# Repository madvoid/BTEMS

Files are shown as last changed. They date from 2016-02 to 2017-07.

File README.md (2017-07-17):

# BTEMS
This is the repository for the BTEMS Sensor Stations. A majority of the documentation is in this file, but some is in the code.

### Uploading Instructions
First, change the `XX` in the filename on line 26 to whatever the BTEMS identifier code is. The current methodology is to use a two digit hexadecimal number. Then, using a 3.3v FTDI programmer such as [this](https://www.adafruit.com/products/284) or [this](https://www.sparkfun.com/products/9873), upload BTEMS.ino to a BTEMS. In the Arduino IDE 'tools' menu, the board should be set to `Arduino Pro or Pro Mini`, the processor should be set to `ATmega328 (3.3V, 8Mhz)`, and the programmer should be set to whatever programmer is used. `AVRISP mkll` often works. The port should be set to whatever port the Arduino is plugged into. The power switch on the BTEMS should be set to off when programming.

### Running Instructions
Place the BTEMS where measurements should take place. Ensure there's an SD card inserted into the SD slot. Turn the switch from 'OFF' to 'ON'. After ~3 seconds, the green LED will turn on and remain lit for ~2 seconds. From then on, the BTEMS is running. The green LED should blink every ~10 seconds, implying a measurement was taken. If a red light comes on after turning on, the likely culprit is either the SD card or the real time clock. Make sure the SD card works and has space, and make sure the real time clock works and has a backup battery plugged in.

To turn off, wait until the green LED blinks, then turn the switch from 'ON' to 'OFF' soon after. It is important to wait until the LED is finished blinking to make sure the file is successfully saved.

### File Descriptions
* BTEMS/
 * `BTEMS.ino` - BTEMS arduino sketch
 * `SHT2x.h` - SHT21 library header
 * `SHT2x.cpp` - SHT21 library file
* BTEMS PCB/
 * `BTEMS.brd` - Eagle board file for BTEMS PCB
 * `BTEMS.sch` - Eagle schematic file for BTEMS PCB
 * `BTEMS.*.ger` - BTEMS gerber files for manufacturing
 * `BTEMS.*.xln` - More BTEMS manufacturing files
 * `eagle.epf` - Eagle preferences file
* Data Sheets/
 * Contain part data sheets for posterity
* Matlab Scripts/
 * `Battery_Analysis.m` - Estimates the battery life given certain assumptions.
 * `BTEMS_Plotter.m` - Requests a BTEMS output .csv file from the user and plots some common plots. Very simple
* Radiation Shield/
 * `Radiation_Shield_RevD.*` - The CAD files for the radiation shield. Edit the .SLDPRT file, submit the .STL file for 3D printing, and view the .pdf file. The .STL file can be easily previewed within Github.
 * `SHT_Plug.*` - The CAD files for the plug that holds the SHT21. Edit the .SLDPRT file, submit the .STL file for 3D printing, and view the .pdf file. The .STL file can be easily previewed within Github
* `Bill of Materials.xlsx` - BTEMS bill of materials. Should be 99.9% complete. Missing any mounting hardware or insulation materials.

### Troubleshooting
* Red Light: SD card problem. Is there an SD card? Is it working? Is it formatted? 
 * In one instance, one of the batteries leaked, leaving residue all over the battery holder. The unit would turn on, but a new file would not be able to be created, and the red light would show. After cleaning the residue and replacing the batteries, the unit worked. It is suspected that the residue limited the amount of current available to the unit, which prevented the SD card from working properly.
* No Lights: Possible sensor problem. Are they plugged in? Are they good? Are they plugged in backwards?

### To-Do
1. Measurement validation

### Notes
* Heat ruins the battery life. Outdoor BTEMS will perform poorly compared to the indoor ones.

### Assembly Instructions
1. Solder SD card holder to PCB
2. Solder female RTC header to PCB
3. Solder four male header pins to RTC in the PWR, GND, SCL, SDA holes
4. Solder resistors in corect place
5. Solder power switch in place
6. Solder power screw terminal in place. Make sure screw terminal is straight and fits flush on the PCB!
7. Solder Arduino in place. The programming header on the Arduino should be near on the side of the power switch. Use regular male headers, and the long side of the headers should be pointing up from the board. Make sure all the pins on the Arduino, especially the four pins in the middle of the arduino, are passed through to the PCB.
8. Solder male headers for sensor plug ins in place
   Detail to be added...

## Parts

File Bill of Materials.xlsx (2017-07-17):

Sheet: Full Instrument
Number of Prototypes: |  | 1 | Shipping Costs Not Included! |  |  |  |  |  |  |  |  |  |  |  |  |  |  | BTEMS Required: | 58
Information |  |  |  | Ideal Cost/Unit |  | Ideal Cost/10 Units |  | Ideal Cost/25 Units |  | Ordering |  |  |  | Notes | Cost Percentage Breakdown |  |  | 6/22/2016 Order
Number | Part | Part Name | Quantity/Instrument | Cost/Part | Prototype Cost | Cost/Part | Prototype Cost | Cost/Part | Prototype Cost | Source | Part Number | Package | Link |  | 1 Unit | 10 Units | 25 Units | Quantity Ordered | Cost/Unit | Total Cost
 | Surface Temp Sensor | MLX90614 | 1 | $6.50 | $6.50 | $6.50 | $65.00 | $6.50 | $162.50 | Haoyu Electronics | MLX90614 | Breakout Board | http://www.hotmcu.com/infrared-thermometer-mlx90614-breakout-board-p-223.html?cPath=8 |  | 7.90% | 8.16% | 8.23% | 58 | $6.50 | $377.00
 | Temp/Humidity Sensor | SHT21 | 1 | $11.20 | $11.20 | $11.20 | $112.00 | $11.20 | $280.00 | Ebay | N/A | N/A | http://www.ebay.com/itm/1PCS-SHT21-Digital-Humidity-And-Temperature-Sensor-Module-Replace-SHT15-SHT11-/182103356189 | May need alternates. Not reliable source | 13.61% | 14.05% | 14.18% | 58 | $11.20 | $649.60
 | Waterproof Box | N/A | 1 | $10.50 | $10.50 | $10.50 | $105.00 | $10.50 | $262.50 | Rescue Essentials | 50-0336 | N/A | http://www.rescue-essentials.com/1449-00-xs-polycarbonate-waterproof-case/ |  | 12.76% | 13.17% | 13.30% | 58 | $10.50 | $609.00
 | Real Time Clock | DS3231 | 1 | $13.95 | $13.95 | $12.56 | $125.60 | $12.56 | $314.00 | Adafruit | 3013 | Breakout Board | https://www.adafruit.com/product/3013 |  | 16.96% | 15.76% | 15.91% | 58 | $12.56 | $728.48
 | Backup Battery | CR1220 | 1 | $0.87 | $0.87 | $0.79 | $7.88 | $0.79 | $19.70 | Mouser | 658-CR1220 | 1220 | http://www.mouser.com/ProductDetail/Panasonic-Battery/CR1220/?qs=sGAEpiMZZMuuBt6TL7D%2f6A7P4Pabhz5g | Much cheaper if bought in quantities of 50+ | 1.06% | 0.99% | 1.00% | 58 | $0.70 | $40.60
 | AA Batteries | N/A | 8 | $0.23 | $1.80 | $0.23 | $18.00 | $0.23 | $45.00 | Mouser | 658-LR6XWA | AA | http://www.mouser.com/ProductDetail/Panasonic-Battery/LR6XWA-B/?qs=sGAEpiMZZMuXcNZ31nzYhcGI0qUUgbjI14kQITT1Veg%3d | Comes in packs of 500. Digikey has same part for cheaper with smaller quantities if necessary | 2.19% | 2.26% | 2.28% | 0 | $0.23 | $0.00
 | Jumper Wires | N/A | 0.2 | $3.95 | $0.79 | $3.56 | $7.12 | $3.56 | $17.80 | Adafruit | 794 | N/A | https://www.adafruit.com/products/794 | Comes in packs of 40. Only need 8 per BTEMS | 0.96% | 0.89% | 0.90% | 12 | $3.56 | $42.72
 | 4x AA Battery Holder | N/A | 2 | $1.15 | $2.30 | $1.06 | $21.20 | $1.06 | $53.00 | Mouser | 12BH348-GR | N/A | http://www.mouser.com/ProductDetail/Eagle-Plastic-Devices/12BH348-GR/ | Much cheaper if bought in quantities of 100+ | 2.80% | 2.66% | 2.68% | 116 | $0.90 | $104.86
 | SD Card | N/A | 1 | $3.60 | $3.60 | $3.60 | $36.00 | $3.60 | $90.00 | Newegg | 9SIA1EK0HR9980 | Micro SD with Regular Adapter | http://www.newegg.com/Product/Product.aspx?Item=9SIA1EK0HR9980 | Micro SD card but comes with standard size adapter - Not reliable source | 4.38% | 4.52% | 4.56% | 58 | $3.60 | $208.80
 | Full Shield | N/A | 1 | $24.45 | $24.45 | $23.62 | $236.18 | $22.89 | $572.33 | See 'Shield Parts' | N/A | N/A |  | See 'Shield Parts' Sheet for details | 29.72% | 29.63% | 28.99% | N/A | $0.00 | $778.59
 | Break Away Headers - Right Angle | N/A | 0.1 | $1.95 | $0.20 | $1.95 | $1.95 | $1.85 | $4.63 | Sparkfun | PRT-00553 | N/A | https://www.sparkfun.com/products/553 | Comes in strips of 40, currently only need 4/board. Actually used for SHT21 breakout. Other sensor comes with headers | 0.24% | 0.24% | 0.23% | 6 | $1.95 | $11.70
 | Radiation Shield | N/A | 1 | $6.00 | $6.00 | $6.00 | $60.00 | $6.00 | $150.00 | UofU MechE Dept. | N/A | N/A |  | Printed from UofU MechE 3D printer. Maybe cheaper elsewhere? | 7.29% | 7.53% | 7.60% | 0 | $6.00 | $0.00
 | Set Screw | N/A | 1 | $0.08 | $0.08 | $0.08 | $0.78 | $0.08 | $1.94 | McMaster-Carr | 91290A111 | M3 0.5 x 6 Socket Head | http://www.mcmaster.com/#91290A111 | Comes in packs of 100 @ $7.78 per pack | 0.09% | 0.10% | 0.10% | 1 | $7.78 | $7.78
 | Plasti-Dip White Spray | N/A | 0.005 | $5.98 | $0.03 | $5.98 | $0.30 | $5.98 | $0.75 | Home Depot | 203286992 | 11 oz. Can | http://www.homedepot.com/p/Plasti-Dip-11-oz-White-General-Purpose-Rubber-Coating-Spray-11207-6/203286992 | Assume 200 BTEMS can be made with one can | 0.04% | 0.04% | 0.04% | 2 | $5.98 | $11.96
 |  |  |  |  | $0.00 |  | $0.00 |  | $0.00 |  |  |  |  |  | 0.00% | 0.00% | 0.00% | 0 |  | $0.00
 |  |  |  |  | $0.00 |  | $0.00 |  | $0.00 |  |  |  |  |  | 0.00% | 0.00% | 0.00% | 0 |  | $0.00
 |  |  |  |  | $0.00 |  | $0.00 |  | $0.00 |  |  |  |  |  | 0.00% | 0.00% | 0.00% | 0 |  | $0.00
 |  |  |  |  | $0.00 |  | $0.00 |  | $0.00 |  |  |  |  |  | 0.00% | 0.00% | 0.00% | 0 |  | $0.00
 |  |  |  |  | $0.00 |  | $0.00 |  | $0.00 |  |  |  |  |  | 0.00% | 0.00% | 0.00% | 0 |  | $0.00
 |  |  |  |  | $0.00 |  | $0.00 |  | $0.00 |  |  |  |  |  | 0.00% | 0.00% | 0.00% | 0 |  | $0.00
 |  |  |  |  | $0.00 |  | $0.00 |  | $0.00 |  |  |  |  |  | 0.00% | 0.00% | 0.00% | 0 |  | $0.00
 |  |  |  |  | $0.00 |  | $0.00 |  | $0.00 |  |  |  |  |  | 0.00% | 0.00% | 0.00% | 0 |  | $0.00
 |  |  |  |  | $0.00 |  | $0.00 |  | $0.00 |  |  |  |  |  | 0.00% | 0.00% | 0.00% | 0 |  | $0.00
 |  |  |  |  | $0.00 |  | $0.00 |  | $0.00 |  |  |  |  |  | 0.00% | 0.00% | 0.00% | 0 |  | $0.00
 |  |  |  |  | $0.00 |  | $0.00 |  | $0.00 |  |  |  |  |  | 0.00% | 0.00% | 0.00% | 0 |  | $0.00
 |  |  |  |  | $0.00 |  | $0.00 |  | $0.00 |  |  |  |  |  | 0.00% | 0.00% | 0.00% | 0 |  | $0.00
 |  |  |  |  | $0.00 |  | $0.00 |  | $0.00 |  |  |  |  |  | 0.00% | 0.00% | 0.00% | 0 |  | $0.00
 |  |  |  | Total Prototype Cost: | $82.26 | Total Prototype Cost: | $797.01 | Total Prototype Cost: | $1974.14 |  |  |  |  |  | 100.00% | 100.00% | 100.00% |  | Total Order Cost: | $3571.10
 |  |  |  | Prototype Cost/Unit: | $82.26 | Prototype Cost/Unit: | $79.70 | Prototype Cost/Unit: | $78.97

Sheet: Shield Parts
Number of Prototypes: |  | 1 | Shipping Costs Not Included! |  |  |  |  |  |  |  |  |  |  |  |  |  |  | BTEMS Required: | 58
Information |  |  |  | Ideal Cost/Unit |  | Ideal Cost/10 Units |  | Ideal Cost/25 Units |  | Ordering |  |  |  | Notes | Cost Percentage Breakdown |  |  | 6/22/2016 Order
Number | EAGLE Schematic Name | Part Name | Quantity/Board | Cost/Part | Prototype Cost | Cost/Part | Prototype Cost | Cost/Part | Prototype Cost | Source | Part Number | Package | Link |  | 1 Unit | 10 Units | 25 Units | Quantity Ordered | Cost/Unit | Total Cost
 | N/A | Arduino Pro Mini | 1 | $9.95 | $9.95 | $9.45 | $94.50 | $8.96 | $224.00 | Sparkfun | DEV-11114 | N/A | https://www.sparkfun.com/products/11114 | 3.3V/8MHz Version | 40.70% | 40.01% | 39.14% | 12 | $9.45 | $113.40
 | S1 | SPDT Switch | 1 | $1.50 | $1.50 | $1.50 | $15.00 | $1.43 | $35.75 | Sparkfun | COM-00102 | N/A | https://www.sparkfun.com/products/102 |  | 6.13% | 6.35% | 6.25% | 58 | $1.43 | $82.94
 | SDSLOT | SD Card Holder | 1 | $1.39 | $1.39 | $1.39 | $13.90 | $1.39 | $34.75 | Newark | 35R2925 | N/A | http://www.newark.com/te-connectivity/2041021-3/memory-card-connector-sd-9-position/dp/35R2925?CMP=AFC-QO1721829242?gross_price= | Check if http://tinyurl.com/jfml5gb is the same part | 5.69% | 5.89% | 6.07% | 58 | $1.39 | $80.62
 | RTC_HEADER | Real Time Clock Female Header | 1 | $0.50 | $0.50 | $0.50 | $5.00 | $0.48 | $12.00 | Sparkfun | PRT-11894 | 6-Pin 0.1" Through Hole Header | https://www.sparkfun.com/products/11894 |  | 2.04% | 2.12% | 2.10% | 58 | $0.48 | $27.84
 | BAT_HEADER | Battery Screw Terminal | 1 | $0.43 | $0.43 | $0.43 | $4.30 | $0.36 | $8.92 | Mouser | 571-1776275-2 | N/A | http://www.mouser.com/ProductDetail/Tyco-Electronics-AMP/1776275-2/?qs=sGAEpiMZZMvlOED0T0kTWgFfIGjizkkz | Should also be sold at sparkfun, https://www.sparkfun.com/products/8084 | 1.76% | 1.82% | 1.56% | 58 | $0.33 | $18.97
 | N/A | Break Away Headers - Straight | 1 | $1.50 | $1.50 | $1.50 | $15.00 | $1.43 | $35.75 | Sparkfun | PRT-00116 | 40-Pin 0.1" Breakaway Header | https://www.sparkfun.com/products/116 | Comes in strips of 40, currently only need 34. Prices will be updated once precise count is established | 6.13% | 6.35% | 6.25% | 58 | $1.43 | $82.94
 | RED_LED | Red LED | 1 | $0.13 | $0.13 | $0.08 | $0.79 | $0.08 | $1.98 | Mouser | 604-WP710A10ID | T-1 (3 mm) | http://www.mouser.com/ProductDetail/Kingbright/WP710A10ID/?qs=sGAEpiMZZMtmwHDZQCdlqbkQSv8HD28QuawgpDquR1I%3d | 2V forward voltage | 0.53% | 0.33% | 0.35% | 58 | $0.08 | $4.58
 | GREEN_LED | Green LED | 1 | $0.14 | $0.14 | $0.09 | $0.86 | $0.09 | $2.15 | Mouser | 604-WP710A10GD | T-1 (3 mm) | http://www.mouser.com/ProductDetail/Kingbright/WP710A10GD/?qs=sGAEpiMZZMtmwHDZQCdlqbkQSv8HD28Qk0jBElTDvNI%3d | 2.2V forward voltage | 0.57% | 0.36% | 0.38% | 58 | $0.86 | $49.88
 | R_RLED | 270 Ohm Resistor | 1 | $0.10 | $0.10 | $0.03 | $0.29 | $0.03 | $0.73 | Mouser | 279-CFR25J270R | N/A | http://www.mouser.com/ProductDetail/TE-Connectivity-Neohm/CFR25J270R/ | 3.3V supply, 2V voltage drop, 5mA forward current. For red LED. Check package size | 0.41% | 0.12% | 0.13% | 58 | $0.03 | $1.68
 | R_GLED | 220 Ohm Resistor | 1 | $0.12 | $0.12 | $0.02 | $0.20 | $0.02 | $0.45 | Mouser | 588-OK2215E-R52 | N/A | http://www.mouser.com/ProductDetail/Ohmite/OK2215E-R52/?qs=sGAEpiMZZMtlubZbdhIBIJMLE6vvLglcwrpJO6Dxohs%3d | 3.3V supply, 2.2V voltage drop, 5mA forward current. For green LED | 0.49% | 0.08% | 0.08% | 58 | $0.01 | $0.87
 | R1 | 24k Ohm Resistor | 1 | $0.12 | $0.12 | $0.09 | $0.92 | $0.09 | $2.30 | Mouser | 603-MFR-25FTE52-24K | N/A | http://www.mouser.com/ProductDetail/Yageo/MFR-25FTE52-24K/ | 4x AA batteries for 6V total in series at max. Voltage divider down to 3.3V for Arduino analag read | 0.49% | 0.39% | 0.40% | 58 | $0.09 | $5.34
 | R2 | 30k Ohm Resistor | 1 | $0.12 | $0.12 | $0.09 | $0.92 | $0.09 | $2.30 | Mouser | MFR-25FBF52-30K | N/A | http://www.mouser.com/ProductDetail/Yageo/MFR-25FBF52-30K/?qs=sGAEpiMZZMsPqMdJzcrNwvki5I7GwxKexr3bQCDZBCM%3d | 4x AA batteries for 6V total in series at max. Voltage divider down to 3.3V for Arduino analag read | 0.49% | 0.39% | 0.40% | 58 | $0.09 | $5.34
 | N/A | Printed Circuit Board | 1 | $8.45 | $8.45 | $8.45 | $84.50 | $8.45 | $211.25 | OshPark | N/A | N/A |  | 2"x2.5" board. $5/in^2 for regular order, $1/in^2 for medium run. | 34.56% | 35.78% | 36.91% | 60 | $5.07 | $304.20
 |  |  |  |  | $0.00 |  | $0.00 |  | $0.00 |  |  |  |  |  | 0.00% | 0.00% | 0.00% | 0 |  | $0.00
 |  |  |  |  | $0.00 |  | $0.00 |  | $0.00 |  |  |  |  |  | 0.00% | 0.00% | 0.00% | 0 |  | $0.00
 |  |  |  |  | $0.00 |  | $0.00 |  | $0.00 |  |  |  |  |  | 0.00% | 0.00% | 0.00% | 0 |  | $0.00
 |  |  |  |  | $0.00 |  | $0.00 |  | $0.00 |  |  |  |  |  | 0.00% | 0.00% | 0.00% | 0 |  | $0.00
 |  |  |  |  | $0.00 |  | $0.00 |  | $0.00 |  |  |  |  |  | 0.00% | 0.00% | 0.00% | 0 |  | $0.00
 |  |  |  |  | $0.00 |  | $0.00 |  | $0.00 |  |  |  |  |  | 0.00% | 0.00% | 0.00% | 0 |  | $0.00
 |  |  |  |  | $0.00 |  | $0.00 |  | $0.00 |  |  |  |  |  | 0.00% | 0.00% | 0.00% | 0 |  | $0.00
 |  |  |  |  | $0.00 |  | $0.00 |  | $0.00 |  |  |  |  |  | 0.00% | 0.00% | 0.00% | 0 |  | $0.00
 |  |  |  |  | $0.00 |  | $0.00 |  | $0.00 |  |  |  |  |  | 0.00% | 0.00% | 0.00% | 0 |  | $0.00
 |  |  |  |  | $0.00 |  | $0.00 |  | $0.00 |  |  |  |  |  | 0.00% | 0.00% | 0.00% | 0 |  | $0.00
 |  |  |  |  | $0.00 |  | $0.00 |  | $0.00 |  |  |  |  |  | 0.00% | 0.00% | 0.00% | 0 |  | $0.00
 |  |  |  |  | $0.00 |  | $0.00 |  | $0.00 |  |  |  |  |  | 0.00% | 0.00% | 0.00% | 0 |  | $0.00
 |  |  |  |  | $0.00 |  | $0.00 |  | $0.00 |  |  |  |  |  | 0.00% | 0.00% | 0.00% | 0 |  | $0.00
 |  |  |  |  | $0.00 |  | $0.00 |  | $0.00 |  |  |  |  |  | 0.00% | 0.00% | 0.00% | 0 |  | $0.00
 |  |  |  | Total Prototype Cost: | $24.45 | Total Prototype Cost: | $236.18 | Total Prototype Cost: | $572.33 |  |  |  |  |  | 100.00% | 100.00% | 100.00% |  | Total Order Cost: | $778.59
 |  |  |  | Prototype Cost/Unit: | $24.45 | Prototype Cost/Unit: | $23.62 | Prototype Cost/Unit: | $22.89

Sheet: To Add
Rough List

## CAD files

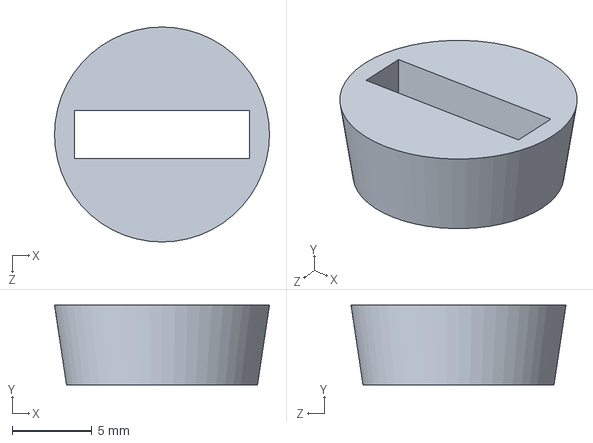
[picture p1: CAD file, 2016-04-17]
Radiation Shield/SHT_Plug.SLDPRT
13.5 x 5.00 x 13.5 mm

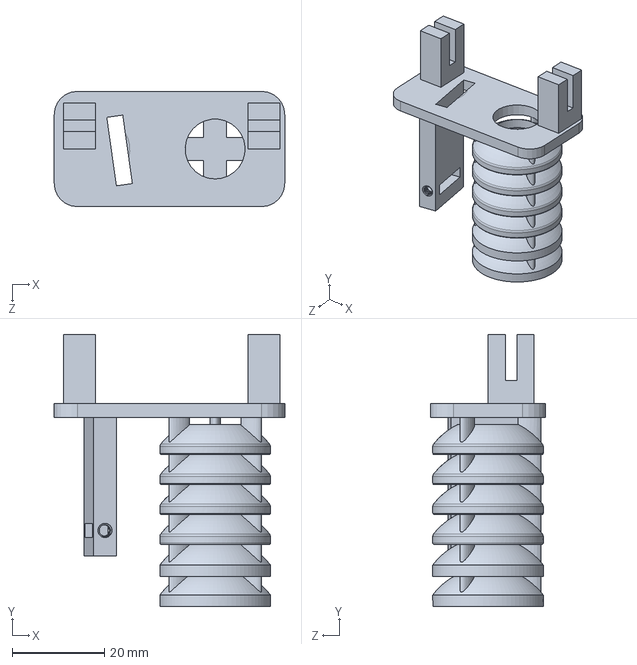
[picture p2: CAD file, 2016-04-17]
Radiation Shield/Radiation_Shield_RevD.SLDPRT
50.0 x 59.0 x 25.0 mm

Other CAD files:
Radiation Shield/Radiation_Shield_RevD.STL
Radiation Shield/SHT_Plug.STL

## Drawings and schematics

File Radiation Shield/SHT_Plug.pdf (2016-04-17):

11

5

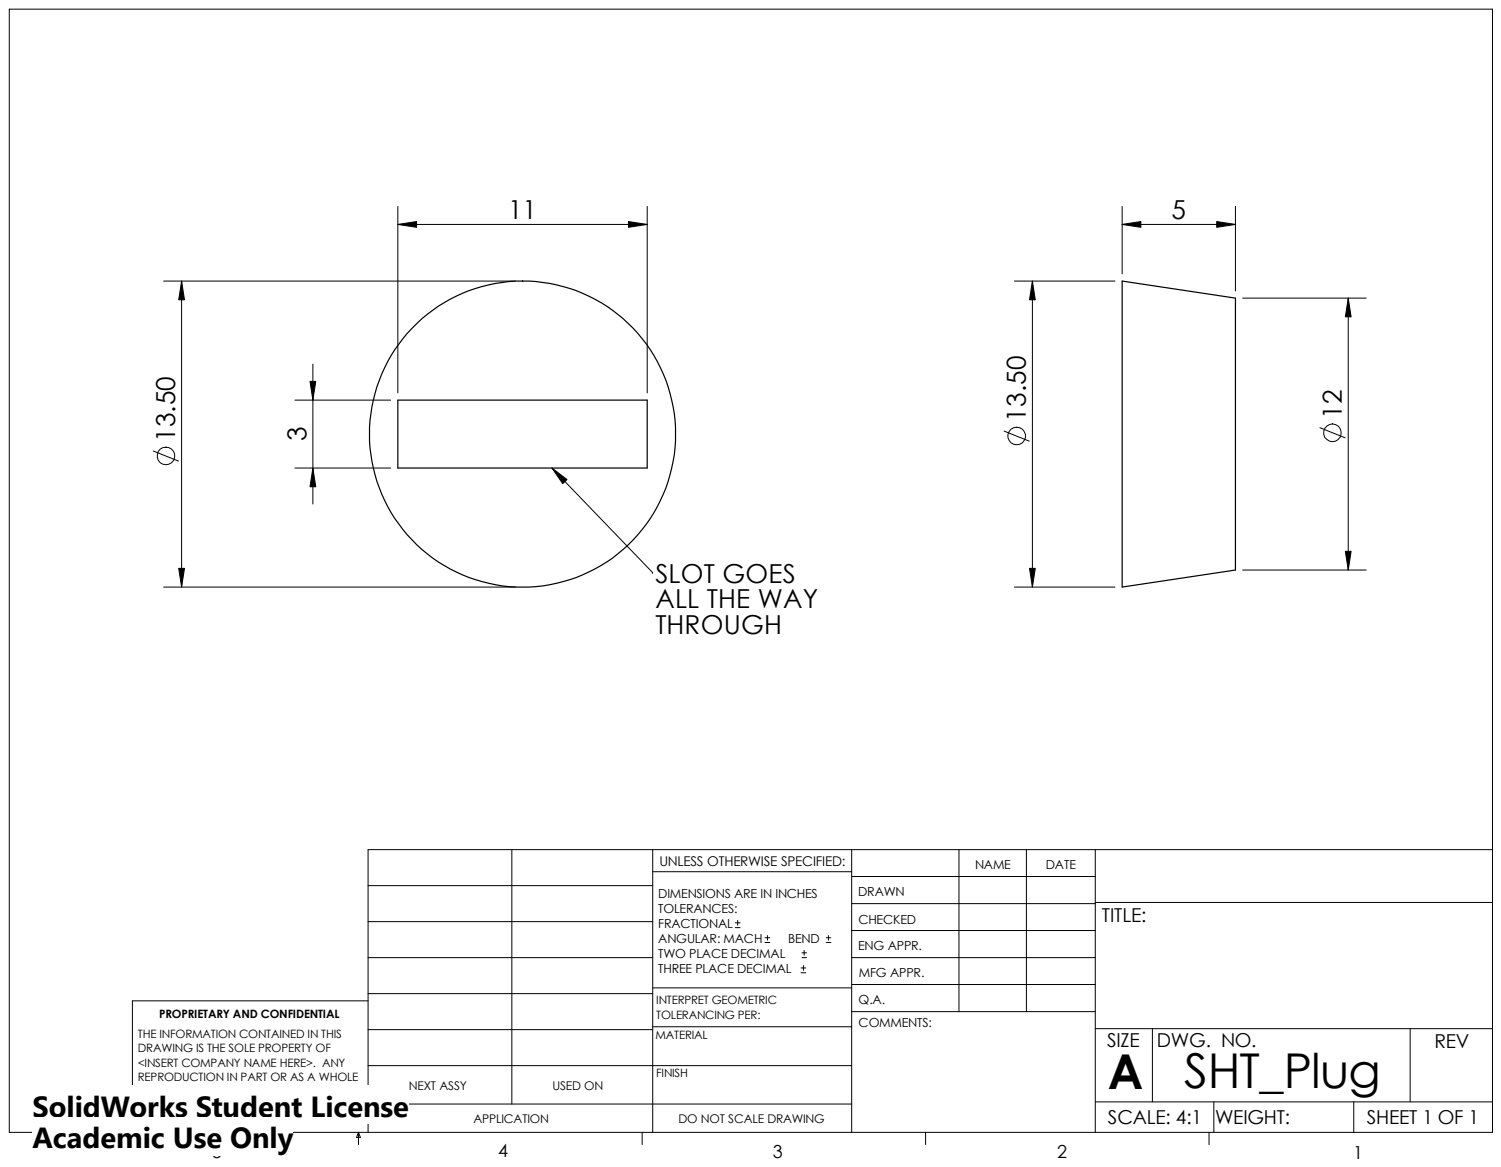
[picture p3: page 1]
COMMENTS:; BEND

SLOT GOES
ALL THE WAY
THROUGH

UNLESS OTHERWISE SPECIFIED: | | NAME | DATE

DIMENSIONS ARE IN INCHES
TOLERANCES:
FRACTIONAL
ANGULAR: MACH
TWO PLACE DECIMAL
THREE PLACE DECIMAL

DRAWN
CHECKED | | | TITLE:

ENG APPR.

MFG APPR.

INTERPRET GEOMETRIC TOLERANCING PER: | Q.A.
MATERIAL | | SIZE A | DWG. NO. SHT_Plug | REV

PROPRIETARY AND CONFIDENTIAL
THE INFORMATION CONTAINED IN THIS
DRAWING IS THE SOLE PROPERTY OF
<INSERT COMPANY NAME HERE>. ANY
REPRODUCTION IN PART OR AS A WHOLE
WITHOUT THE WRITTEN PERMISSION OF
<INSERT COMPANY NAME HERE> IS
PROHIBITED.

NEXT ASSY | USED ON | FINISH

SolidWorks Student License
Academic Use Only

APPLICATION | DO NOT SCALE DRAWING | | SCALE: 4:1 | WEIGHT: | SHEET 1 OF 1

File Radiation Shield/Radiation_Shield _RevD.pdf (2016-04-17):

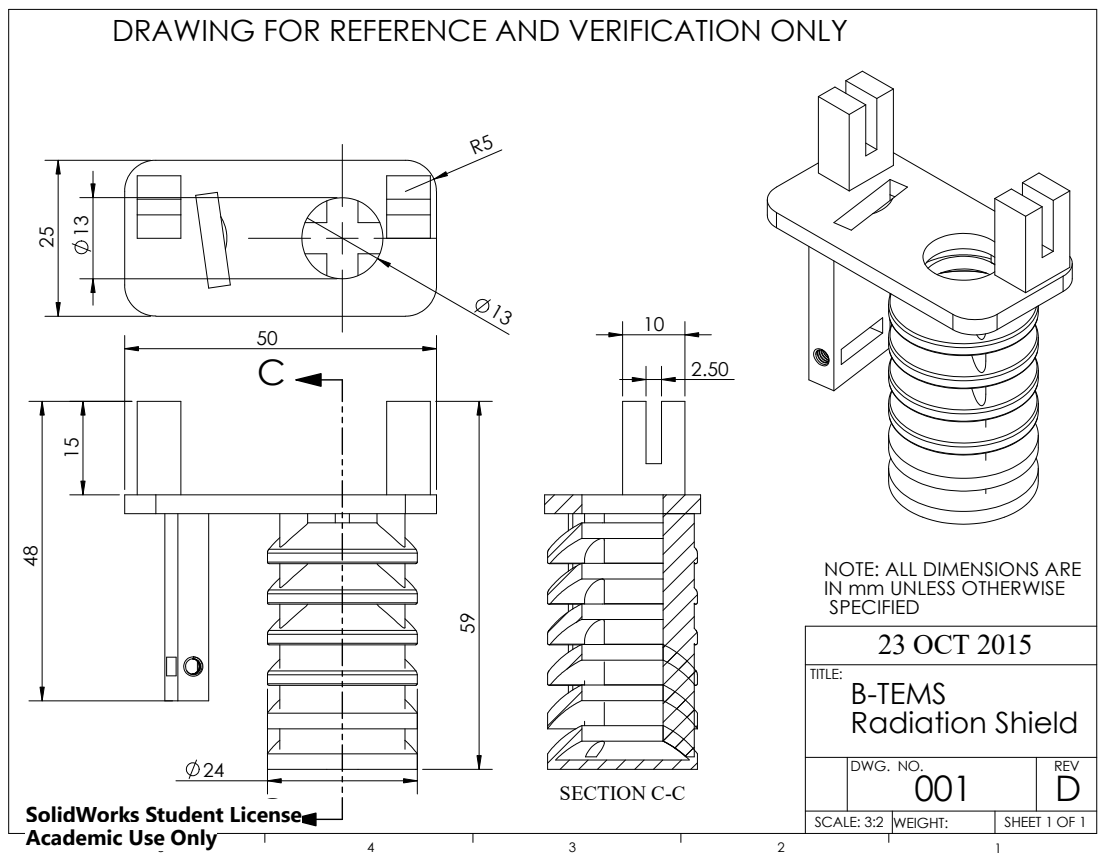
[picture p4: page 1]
B-TEMS Radiation Shield; TITLE:; SECTION C-C

DRAWING FOR REFERENCE AND VERIFICATION ONLY

NOTE: ALL DIMENSIONS ARE
IN mm UNLESS OTHERWISE
SPECIFIED
23 OCT 2015

DWG. NO. 001 | REV D

SolidWorks Student License C
Academic Use Only

SCALE: 3:2 | WEIGHT: | SHEET 1 OF 1

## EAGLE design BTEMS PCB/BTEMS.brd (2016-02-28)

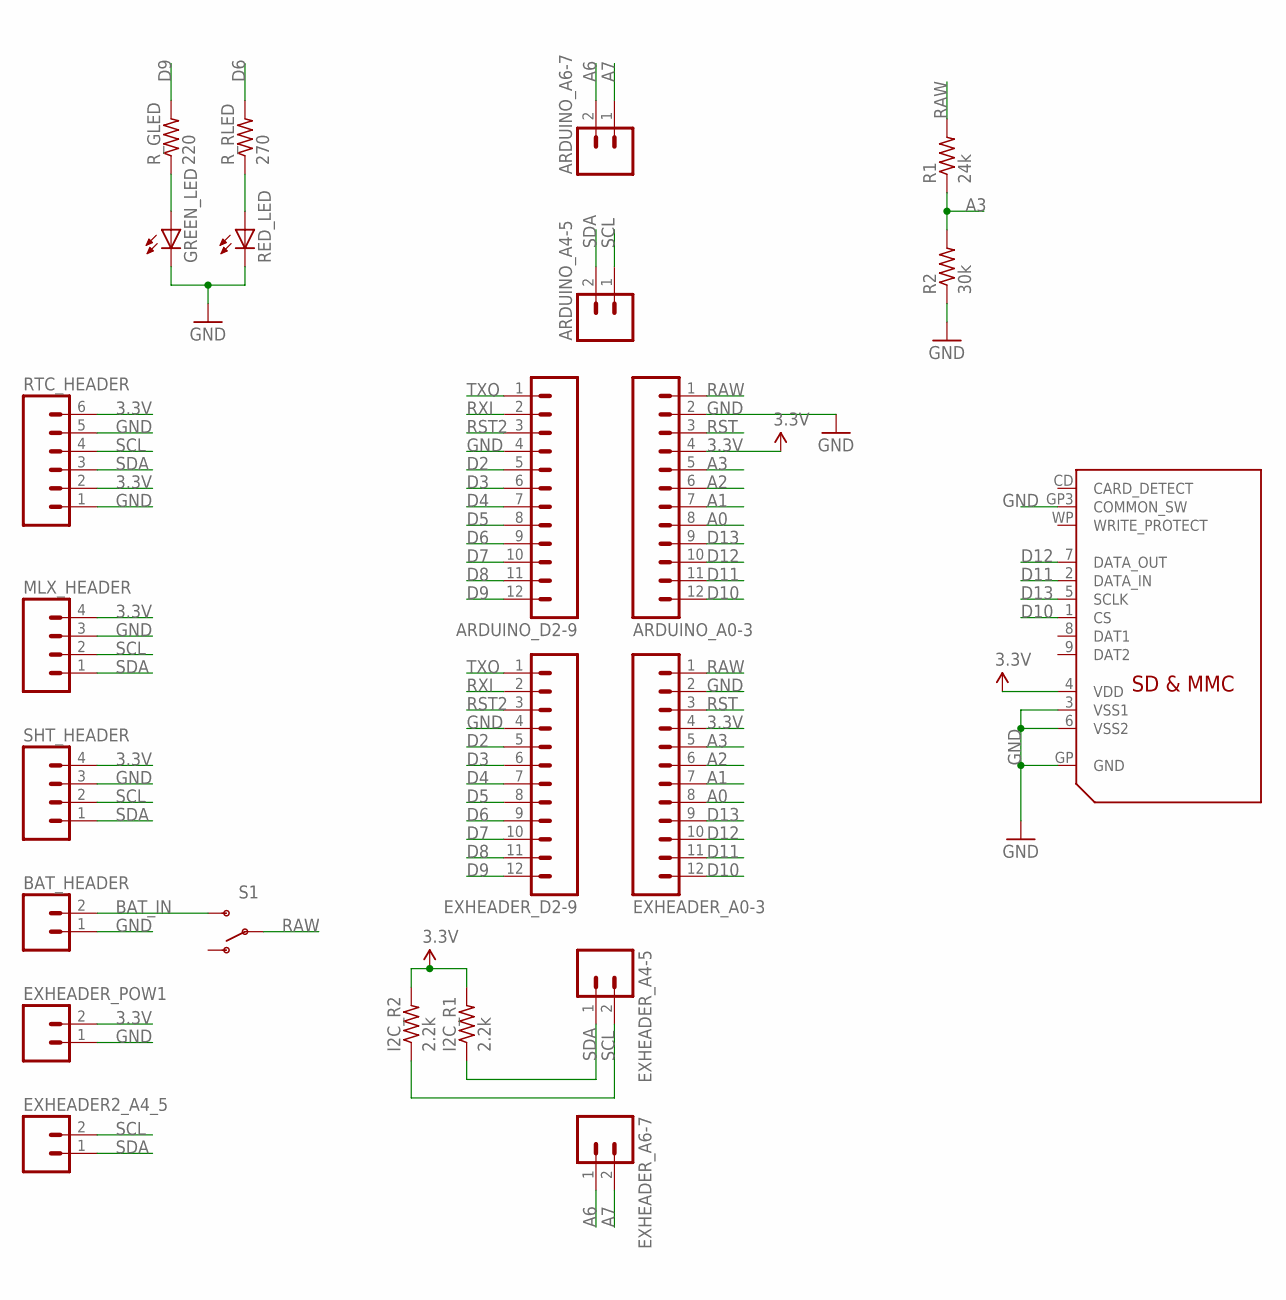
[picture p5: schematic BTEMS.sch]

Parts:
ARDUINO_A0-3: M12LOCK; 1X12_LOCK
ARDUINO_A4-5, ARDUINO_A6-7: M02PTH; 1X02
ARDUINO_D2-9: M12LOCK; 1X12_LOCK
BAT_HEADER: M023.5MM; SCREWTERMINAL-3.5MM-2
EXHEADER2_A4_5: M02PTH; 1X02
EXHEADER_A0-3: M12PTH; 1X12
EXHEADER_A4-5, EXHEADER_A6-7: M02LOCK; 1X02_LOCK
EXHEADER_D2-9: M12PTH; 1X12
EXHEADER_POW1: M02PTH; 1X02
GREEN_LED: LED3MM
I2C_R1, I2C_R2: 2.2k; 0207/7
MLX_HEADER: M04LOCK; 1X04_LOCK
R1: 24k; 0207/7
R2: 30k; 0207/7
RED_LED: LED3MM
RTC_HEADER: M06FEMALE_LOCK; 1X06_FEMALE_LOCK.010
R_GLED: 220; 0207/7
R_RLED: 270; 0207/7
S1: SWITCH-SPDTPTH; SWITCH-SPDT
SDSLOT: SDMMC06132; 06132
SHT_HEADER: M04LOCK; 1X04_LOCK

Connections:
3.3V: ARDUINO_A0-3.4, EXHEADER_A0-3.4, EXHEADER_POW1.2, I2C_R1.2, I2C_R2.2, MLX_HEADER.4, RTC_HEADER.2, RTC_HEADER.6, SDSLOT.4 (VDD), SHT_HEADER.4
A0: ARDUINO_A0-3.8, EXHEADER_A0-3.8
A1: ARDUINO_A0-3.7, EXHEADER_A0-3.7
A2: ARDUINO_A0-3.6, EXHEADER_A0-3.6
A3: ARDUINO_A0-3.5, EXHEADER_A0-3.5, R1.1, R2.2
A6: ARDUINO_A6-7.2, EXHEADER_A6-7.1
A7: ARDUINO_A6-7.1, EXHEADER_A6-7.2
BAT_IN: BAT_HEADER.2, S1.3 (S)
D2: ARDUINO_D2-9.5, EXHEADER_D2-9.5
D3: ARDUINO_D2-9.6, EXHEADER_D2-9.6
D4: ARDUINO_D2-9.7, EXHEADER_D2-9.7
D5: ARDUINO_D2-9.8, EXHEADER_D2-9.8
D6: ARDUINO_D2-9.9, EXHEADER_D2-9.9, R_RLED.2
D7: ARDUINO_D2-9.10, EXHEADER_D2-9.10
D8: ARDUINO_D2-9.11, EXHEADER_D2-9.11
D9: ARDUINO_D2-9.12, EXHEADER_D2-9.12, R_GLED.2
D10: ARDUINO_A0-3.12, EXHEADER_A0-3.12, SDSLOT.1 (CS)
D11: ARDUINO_A0-3.11, EXHEADER_A0-3.11, SDSLOT.2 (DATA_IN)
D12: ARDUINO_A0-3.10, EXHEADER_A0-3.10, SDSLOT.7 (DATA_OUT)
D13: ARDUINO_A0-3.9, EXHEADER_A0-3.9, SDSLOT.5 (SCLK)
GND: ARDUINO_A0-3.2, ARDUINO_D2-9.4, BAT_HEADER.1, EXHEADER_A0-3.2, EXHEADER_D2-9.4, EXHEADER_POW1.1, GREEN_LED.K (C), MLX_HEADER.3, R2.1, RED_LED.K (C), RTC_HEADER.1, RTC_HEADER.5, SDSLOT.3 (VSS1), SDSLOT.6 (VSS2), SDSLOT.GP (GND), SDSLOT.GP3 (COMMON_SW), SHT_HEADER.3
unnamed: GREEN_LED.A, R_GLED.1
unnamed: RED_LED.A, R_RLED.1
RAW: ARDUINO_A0-3.1, EXHEADER_A0-3.1, R1.2, S1.2
RST: ARDUINO_A0-3.3, EXHEADER_A0-3.3
RST2: ARDUINO_D2-9.3, EXHEADER_D2-9.3
RXI: ARDUINO_D2-9.2, EXHEADER_D2-9.2
SCL: ARDUINO_A4-5.1, EXHEADER2_A4_5.2, EXHEADER_A4-5.2, I2C_R2.1, MLX_HEADER.2, RTC_HEADER.4, SHT_HEADER.2
SDA: ARDUINO_A4-5.2, EXHEADER2_A4_5.1, EXHEADER_A4-5.1, I2C_R1.1, MLX_HEADER.1, RTC_HEADER.3, SHT_HEADER.1
TXO: ARDUINO_D2-9.1, EXHEADER_D2-9.1

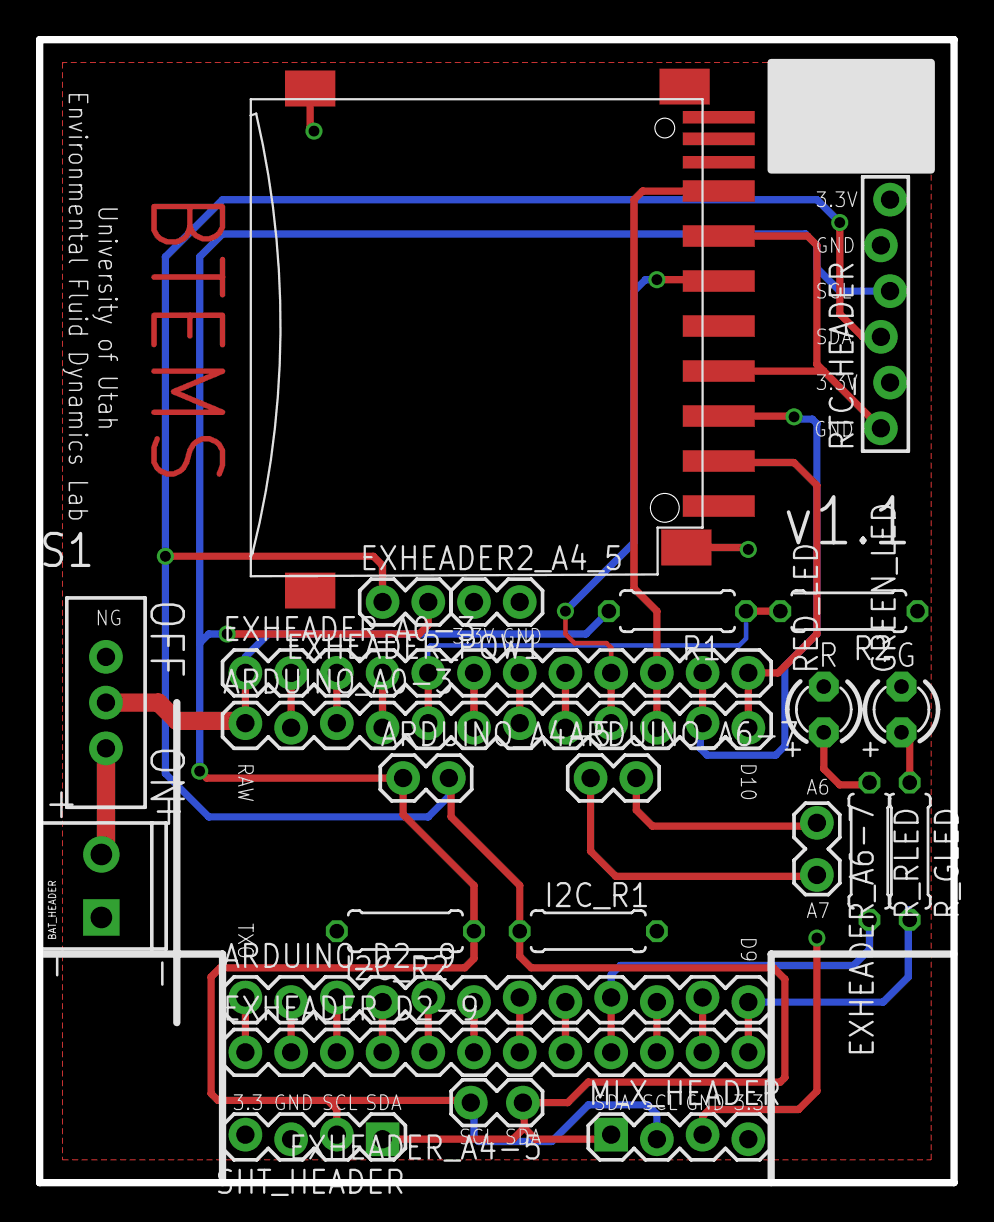
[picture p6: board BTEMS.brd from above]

Board: 2 copper layers, 50.8 x 63.5 mm, 24 parts (0 on the bottom side), 30 nets.

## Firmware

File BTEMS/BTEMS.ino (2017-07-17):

// ------------------------------------------------------------------------------------------------
// Filename: BTEMS.ino
//
// Authors: Nipun Gunawardena
//          Elizabeth Prucka
//
// Notes:
//   - Tested on Arduino Mini Pro 3.3V
//   - After uploading code, the user should wait until the program has fully started and taken a few
//     readings before unplugging from the computer
//   - Current delay in realtime is a little less than 10 seconds
//   - If four AA batteries are used, the resistor divider should consist of a 24k high-side resistor (R1)
//     and a 30k low-side resistor (R2)
//   - The original SHT2x library repository was deleted, which is why it's included with this code
//
// TODO:
//   - Add support for 999 files
//
// Compile Settings: Board: "Arduino Pro or Pro Mini"
//                   Processor: "ATmega 328 (3.3V, 8MHz)"
//
// Current consumption values:
//   - 3.60 to 4.40 mA during sleep with knockoff RTC
//   - At least 12.5mA during write, assume 20mA-40mA during write
//   - 2.02 mA during sleep with adafruit RTC
//
// ------------------------------------------------------------------------------------------------

// !! Change Filename depending on station. Change the XX below to hexadecimal number !!
char filename[] = "BTM08_00.CSV";     // Prototype filename



// Includes ---------------------------------------------------------------------------------------
#include <Adafruit_MLX90614.h>  // Infrared Temp Library    https://github.com/adafruit/Adafruit-MLX90614-Library
#include <Narcoleptic.h>  // Sleep Library                  https://code.google.com/archive/p/narcoleptic/
#include <RTClib.h>       // RTC Library                    https://github.com/mizraith/RTClib
#include <SD.h>           // SD card                        Included
#include "SHT2x.h"        // SHT21 Library                  Included in same folder            
#include <SPI.h>          // SPI Library                    Included
#include <Wire.h>         // I2C Library                    Included




// Defining ---------------------------------------------------------------------------------------
#define DEBUG 0           // Used to Show Serial Monitor during Debugging
#define RED_LED_PIN 6     // Pin used for red LED
#define GRN_LED_PIN 9     // Pin used for green LED
#define BAT_PIN A3        // Pin used to measure battery level
#define CHIP_SELECT 10    // Chip select pin for SD card




// Initializations --------------------------------------------------------------------------------
float mlxIR;                // IR values from MLX90614
float mlxAmb;               // Ambient temp values from MLX90614
float shtAmb;               // Ambient temp values from SHT21
float shtHum;               // Relative humidity values from SHT21
float mSecs;                // Milliseconds from Arduino
float batLvl;               // Battery voltage level
unsigned int batRaw;        // Raw battery input

const unsigned int R1 = 24000;   // High-side resistor for battery measuring voltage divider
const unsigned int R2 = 30000;   // Low-side resistor for battery measuring voltage divider

Adafruit_MLX90614 mlx = Adafruit_MLX90614();  // MLX90614 Class
RTC_DS3231 RTC;                               // RTC Class

File logfile;               // Data object you will write your sensor data to





// Function Prototypes ----------------------------------------------------------------------------
void error(char *str);                  // Error function prototype
void blinkGreenLED(unsigned long m);    //Blinking Green LED function
void blinkRedLED(unsigned long m);      //Blinking Red LED function




// Setup Function ---------------------------------------------------------------------------------
void setup() {
#if DEBUG
  Serial.begin(9600); //turn on serial monitor
#endif

  // Initialize libraries
  Wire.begin();
  mlx.begin();
  RTC.begin();

  // Initialize SD Card
  SD.begin(CHIP_SELECT);     //Initialize the SD card reader

  //Declare Pins for LED
  pinMode(RED_LED_PIN, OUTPUT);
  pinMode(GRN_LED_PIN, OUTPUT);

  // Create filename, open SD Card File
  for (uint8_t i = 0; i < 100; i++) {            // Indexes file every time program is restarted
    filename[6] = i / 10 + '0';                  // !! Will stop at 99 !!
    filename[7] = i % 10 + '0';
    if (! SD.exists(filename)) {
      logfile = SD.open(filename, FILE_WRITE);
      break;
    }
  }

  // Prepare file
  if (!logfile) {               // File successfully opened check
    error("Couldnt create file!");
  }
  logfile.println("Year, Month, Day, Hour, Minute, Second, SHT_Amb_C, SHT_Hum_Pct, MLX_IR_C, MLX_Amb_C, Bat_Lvl_V"); // Print header to SD
  logfile.flush();             //Save file

  // Print header for debugging
#if DEBUG
  Serial.println("Year, Month, Day, Hour, Minute, Second, SHT_Amb_C, SHT_Hum_Pct, MLX_IR_C, MLX_Amb_C, Bat_Lvl_V");
#endif

  // Check if the RTC is running.
  // TODO: Determine whether chunk is necessary
  // Doesn't work when uncommented, why?
  //  if (! RTC.isrunning()) {
  //    Serial.println("RTC is NOT running");
  //    error("RTC is NOT running");
  //  }

  // Gets current datetime and compares it to compilation time
  DateTime now = RTC.now();
  DateTime compiled = DateTime(__DATE__, __TIME__);
  if (now.unixtime() < compiled.unixtime()) {
    Serial.println("RTC is older than compile time! Updating");
    RTC.adjust(DateTime(__DATE__, __TIME__));
    for (int i = 0; i < 3; i++) {
      blinkRedLED(100);
      blinkGreenLED(100);
    }
  }

  delay(1000);              // Give user time to look at LED
  blinkGreenLED(2000);      // Blink Green LED for 2 seconds
}




// Loop Function ----------------------------------------------------------------------------------
void loop() {

  // Gather measurements
  digitalWrite(GRN_LED_PIN, HIGH);  // Start blink
  shtAmb = SHT2x.GetTemperature();
  mlxAmb = mlx.readAmbientTempC();
  mlxIR = mlx.readObjectTempC();
  shtHum = SHT2x.GetHumidity();

  batRaw = 0;
  for (int i = 0; i < 3; i++) {
    batRaw += analogRead(BAT_PIN);    // Average battery readings, division happens below
  }

  batLvl = ( ((float)batRaw) * (3.3 / 1024.0 / 3.0) * (float)(R1 + R2) ) / ((float)R2);

  // Get the current time
  DateTime now = RTC.now();

  // Write to SD card
  if (logfile) {
    logfile.print(now.year(), DEC);
    logfile.print(", ");
    logfile.print(now.month(), DEC);
    logfile.print(", ");
    logfile.print(now.day(), DEC);
    logfile.print(", ");
    logfile.print(now.hour(), DEC);
    logfile.print(", ");
    logfile.print(now.minute(), DEC);
    logfile.print(", ");
    logfile.print(now.second(), DEC);
    logfile.print(", ");
    logfile.print(shtAmb);
    logfile.print(", ");
    logfile.print(shtHum);
    logfile.print(", ");
    logfile.print(mlxIR);
    logfile.print(", ");
    logfile.print(mlxAmb);
    logfile.print(", ");
    logfile.print(batLvl);
    logfile.println();
    logfile.flush();                                  //Save file
  }

  // End Blink Green LED
  digitalWrite(GRN_LED_PIN, LOW);

  // Write to Serial Monitor
#if DEBUG
  Serial.print(now.year(), DEC);
  Serial.print(", ");
  Serial.print(now.month(), DEC);
  Serial.print(", ");
  Serial.print(now.day(), DEC);
  Serial.print(", ");
  Serial.print(now.hour(), DEC);
  Serial.print(", ");
  Serial.print(now.minute(), DEC);
  Serial.print(", ");
  Serial.print(now.second(), DEC);
  Serial.print(", ");
  Serial.print(shtAmb);
  Serial.print(", ");
  Serial.print(shtHum);
  Serial.print(", ");
  Serial.print(mlxIR);
  Serial.print(", ");
  Serial.print(mlxAmb);
  Serial.print(", ");
  Serial.print(batLvl);
  Serial.println();
  Serial.flush();
#endif

  // Delay/Sleep
  Narcoleptic.delay(8200);
  // delay(9421);
}




//Blink LED Functions --------------------------------------------------------------------------------
void blinkGreenLED(unsigned long m) {
  //Blinks Green LED
  digitalWrite(GRN_LED_PIN, HIGH);
  delay(m);
  digitalWrite(GRN_LED_PIN, LOW);
}

void blinkRedLED(unsigned long m) {
  //Blinks Red LED
  digitalWrite(RED_LED_PIN, HIGH);
  delay(m);
  digitalWrite(RED_LED_PIN, LOW);
}




//Error Function --------------------------------------------------------------------------------------
void error(const char *str) {
  //Turns on red LED
  digitalWrite(RED_LED_PIN, HIGH);

  //Print Error to Serial Monitor
#if DEBUG
  Serial.print("Error: ");
  Serial.println(str);
#endif

  while (1);
}

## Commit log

2015-10-13 Added functions for LEDs
2016-02-06 Minor changes, added battery checking
2016-02-07 Added several files, minor changes
    [BTEMS.brd, BTEMS.sch]
2016-02-08 Solidified part position, added BOM
    [BTEMS.brd, BTEMS.sch, Bill of Materials.xlsx]
2016-02-09 Routed board
    [BTEMS.brd, BTEMS.sch]
2016-02-09 Added silkscreen, BOM parts
    [BTEMS.brd, BTEMS.sch, Bill of Materials.xlsx]
2016-02-09 Added battery voltage equation
2016-02-11 Many changes and added gerber files
    [BTEMS.GBL, BTEMS.GBO, BTEMS.GBS, BTEMS.GTL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]
2016-02-15 Osh Park Submission
    [BTEMS.GBL, BTEMS.GBS, BTEMS.GTL, BTEMS.brd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]
2016-02-25 Minor changes/Updated todo
    [Bill of Materials.xlsx]
2016-02-26 v1.1 changes added
    [BTEMS.brd, BTEMS.sch, Bill of Materials.xlsx]
2016-02-28 v1.1 final, mostly finished BOM
    [BTEMS.brd, BTEMS.drills.xln, BTEMS.sch, Bill of Materials.xlsx]
2016-03-08 Updated BOM
    [Bill of Materials.xlsx]
2016-04-04 Added plotter code, BTEMS file name changing
    [Bill of Materials.xlsx]
2016-04-05 Minor comment changes
    [Bill of Materials.xlsx]
2016-04-17 Added radiation shield parts
    [Bill of Materials.xlsx, Radiation_Shield.SLDPRT, Radiation_Shield_RevD.STL, SHT_Plug.SLDPRT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]
2016-04-19 Added information to README, file reorganization
    [Radiation_Shield_RevD.SLDPRT]
2016-06-16 Update bill of materials
    [Bill of Materials.xlsx]
2016-06-21 Added schematic names to BOM
    [Bill of Materials.xlsx]
2016-06-22 Added info for 6-22-16 order
    [Bill of Materials.xlsx]
2016-06-23 Final commit before medium run PCB order
    [BTEMS.drills.xln]
2016-06-23 Added PCB costs to BOM
    [BTEMS.drills.xln, Bill of Materials.xlsx]
2016-07-22 Minor notes added
    [Bill of Materials.xlsx]
2017-07-17 Moved SHT2x library to main code folder
    [Bill of Materials.xlsx]

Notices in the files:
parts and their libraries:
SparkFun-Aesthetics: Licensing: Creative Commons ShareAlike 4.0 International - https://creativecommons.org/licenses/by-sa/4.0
